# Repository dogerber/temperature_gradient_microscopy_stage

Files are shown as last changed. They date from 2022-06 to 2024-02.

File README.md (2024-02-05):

# Temperature Gradient Microscopy Stage


Microscopy stage with two temperature controlled metal block and a translational frame to move a sample in the temperature gradient by [D. Gerber](https://orcid.org/0000-0002-4231-0694) from the (now retired) [Soft and Living Materials Group at ETH Zürich](https://softliv.mat.ethz.ch/).

Detailed instructions to build the setup can be found in the [wiki](https://github.com/gerberli/temperature_gradient_microscopy_stage/wiki/).

  > [Building your own setup](https://github.com/dogerber/temperature_gradient_microscopy_stage/wiki/Building-your-own-Setup) 

  > [User manual (softliv group)](https://github.com/gerberli/temperature_gradient_microscopy_stage/wiki/Operation-manual)

This has been used for the following publications: 
* [Stress accumulation by confined ice in a temperature gradient (PNAS)](https://www.pnas.org/doi/10.1073/pnas.2200748119)
* [Polycrystalinity enhances stress build-up around ice (PRL)](https://pubmed.ncbi.nlm.nih.gov/38039453/)
* [Dehydration drives damage in the freezing of brittle hydrogels](https://arxiv.org/abs/2401.12871)

# Setup overview
The setup consists of a PID control loop, where an Arduino microcontroller regulates the voltage for two peltier devices. Thermistors are placed in two copper blocks of variable spacing above the peltier devices and the opposite side of the peltier devices is held at room temperature by water cooling. The sample is placed on the copper block and can be moved relative to the temperature gradient by a linear actuator.

**Stage head**

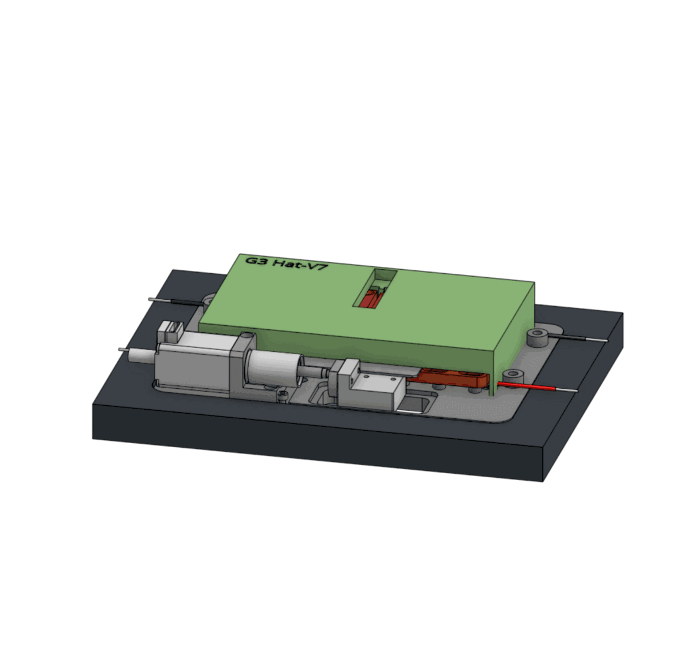
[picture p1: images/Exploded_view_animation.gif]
 
 
 **Controller box**
 
 

**Schematic**

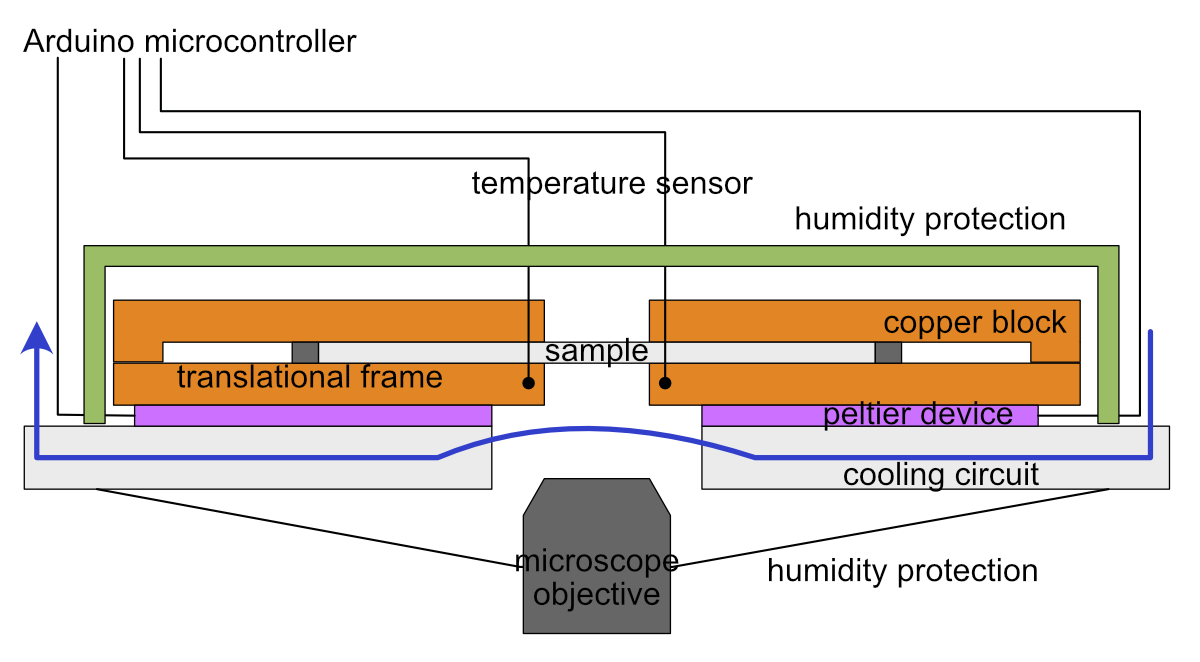
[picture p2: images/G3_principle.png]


# Features
* 0.05 K temperature accuracy, when calibrated
* 0.01 K temperature stability
* Temperature range -25 to 60 °C (colder possible, if using coolant below room temperature)
* Variable spacing between metal blocks of 0-1 cm
* Translation of sample in the temperature gradient with 1.9 cm travel range and 300 nm stepsize
* Optional datalogging to microSD-card
* Optimized for microscope stages with 160x110 mm opening "Universal insert" [I-3091](https://www.asiimaging.com/products/stages-inserts/160-x-110-mm-slide-inserts/), but can be adapted

# Acknowledgement
Lawrence Wilen, Christian Furrer and Robert Style helped with the design of this stage and controller. The menu system used is [GEM](https://github.com/Spirik/GEM) by [Spirik](https://github.com/Spirik).

Inspiration for this stage was also taken from [Prof. Sylvain Devilles group](https://www.sciencedirect.com/science/article/pii/S0304399118300536).

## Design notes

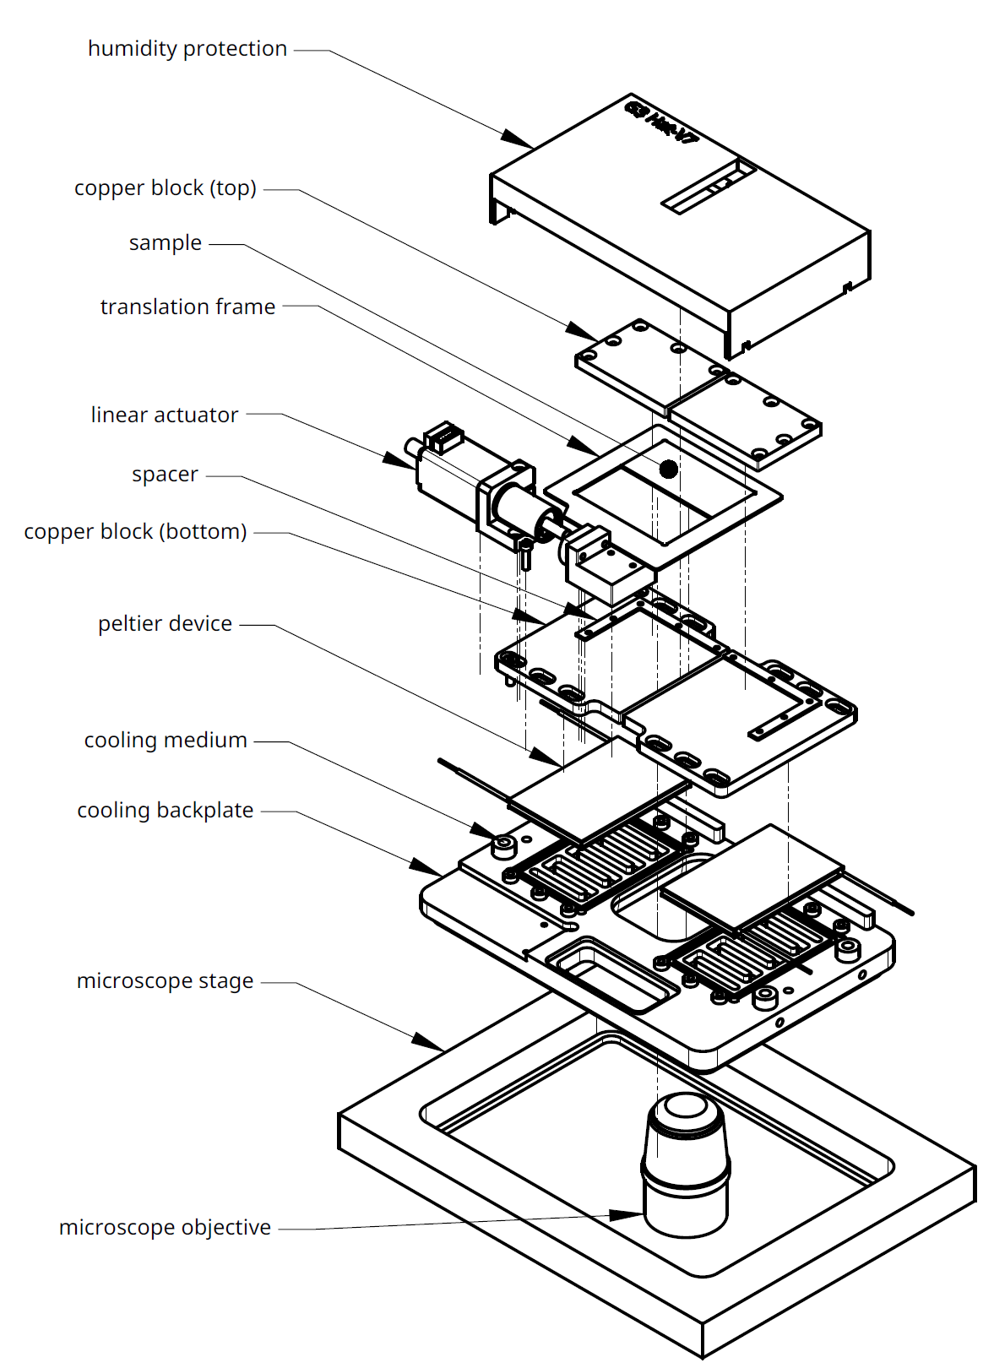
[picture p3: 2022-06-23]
images/stage_head_overview.png

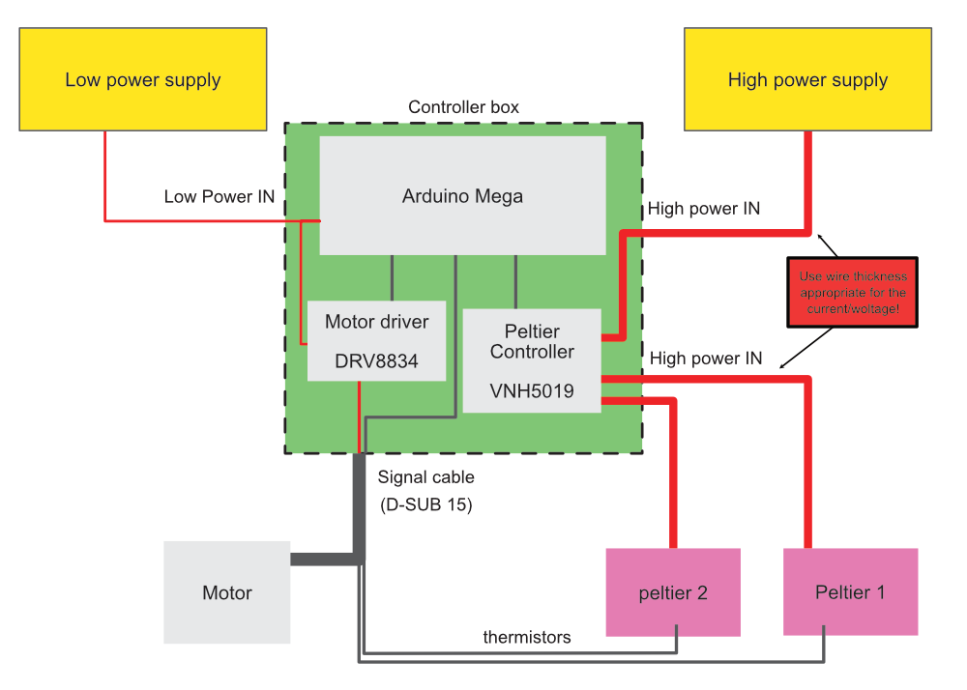
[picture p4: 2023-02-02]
images/power wire schematic.png

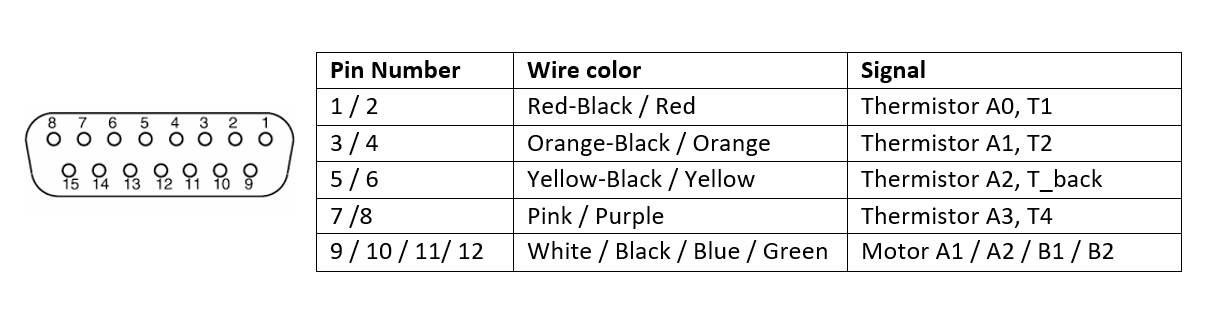
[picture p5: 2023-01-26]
images/dsub-15_pinout.png

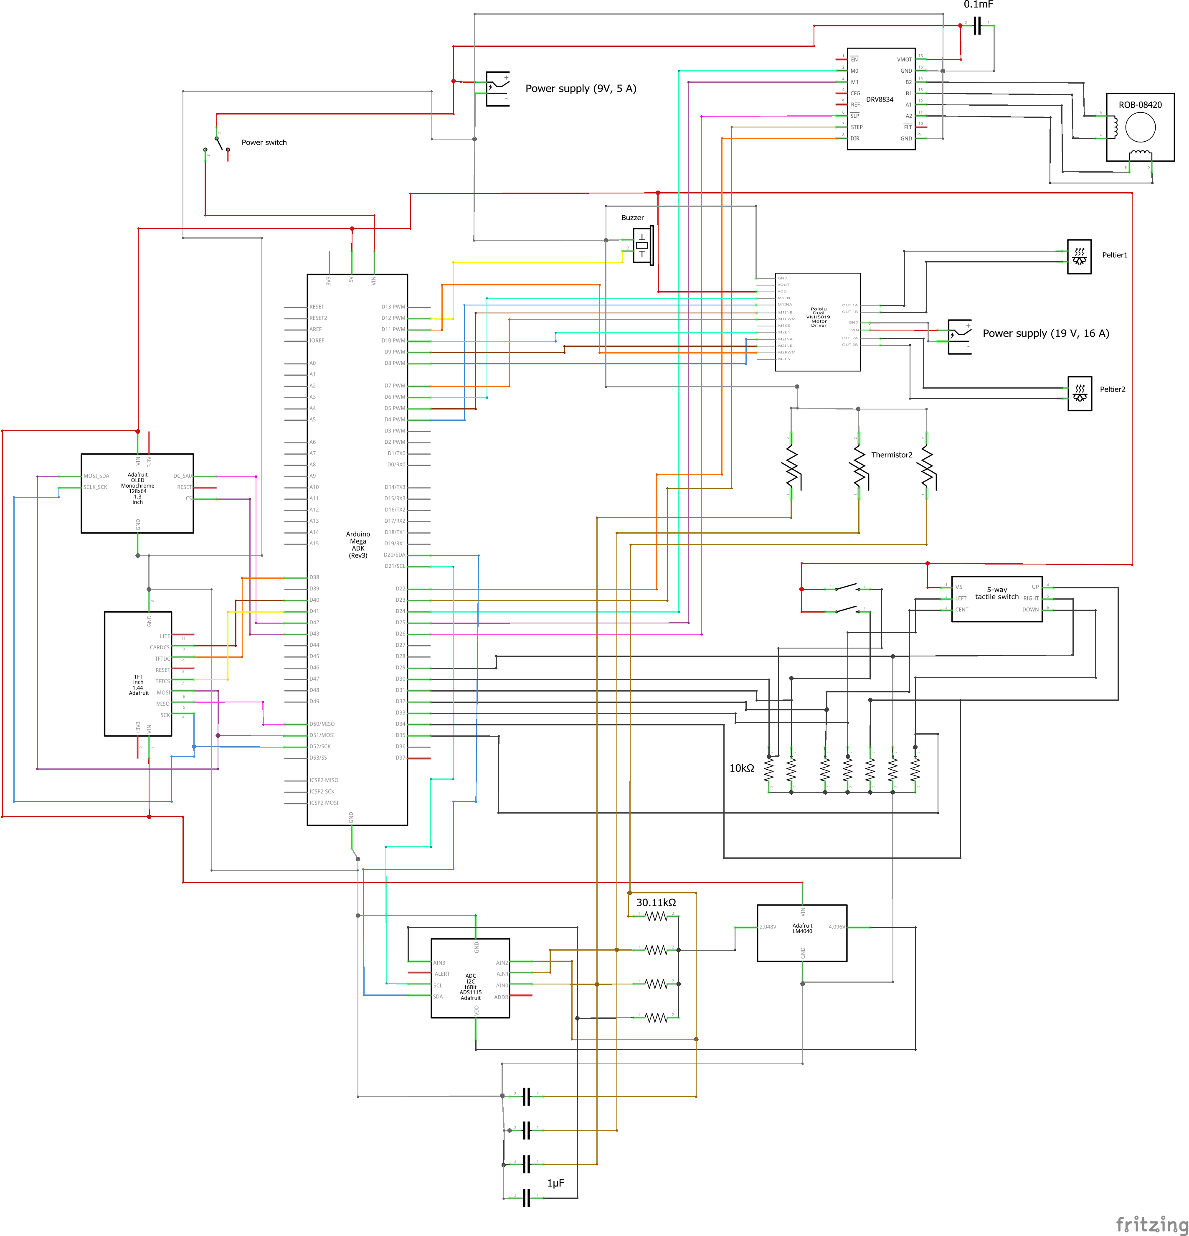
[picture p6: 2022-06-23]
wiring_diagrams/Gelatiera_III_schematic.png

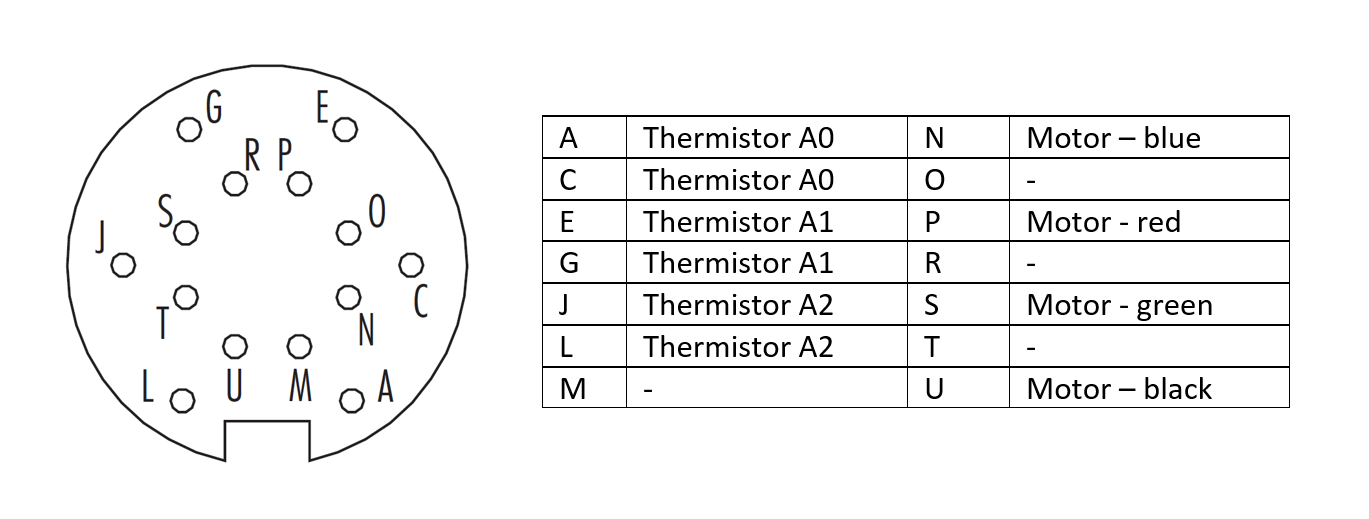
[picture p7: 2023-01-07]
images/signal_cable_layout.png

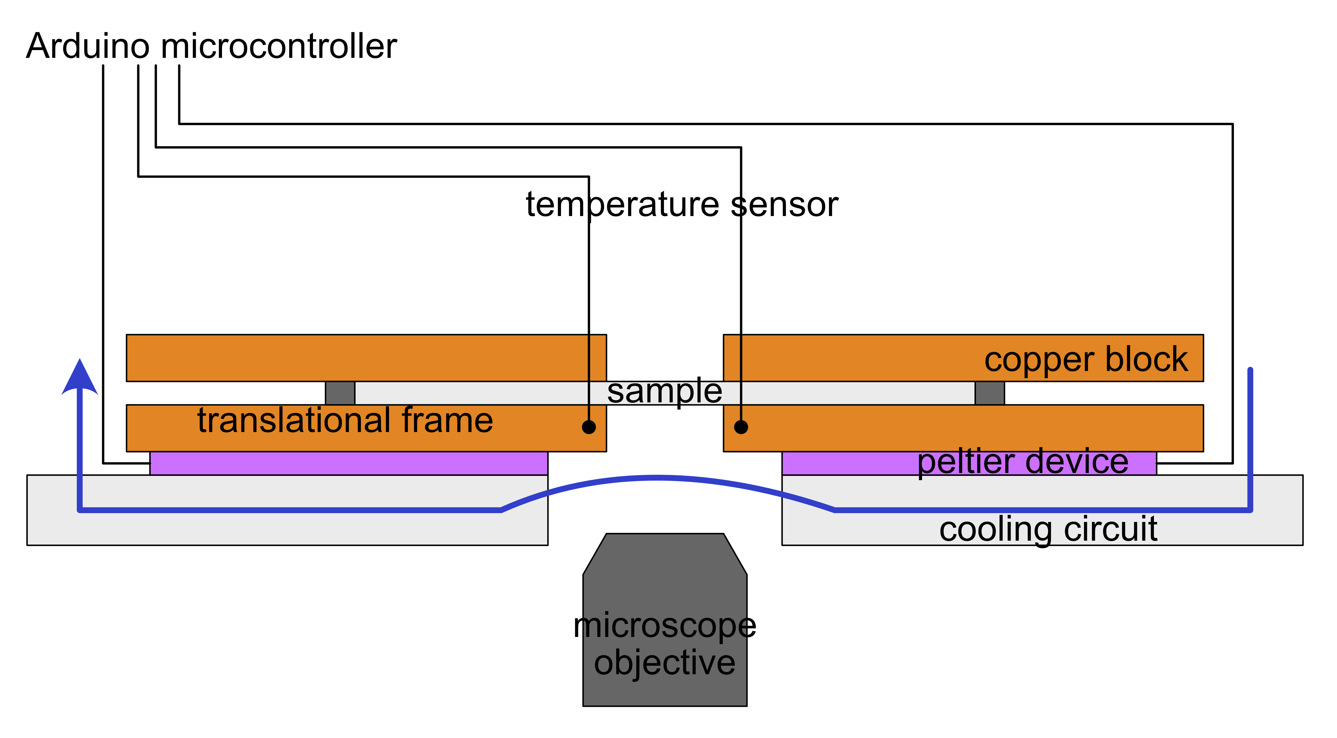
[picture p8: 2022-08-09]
images/G3w_principle.png

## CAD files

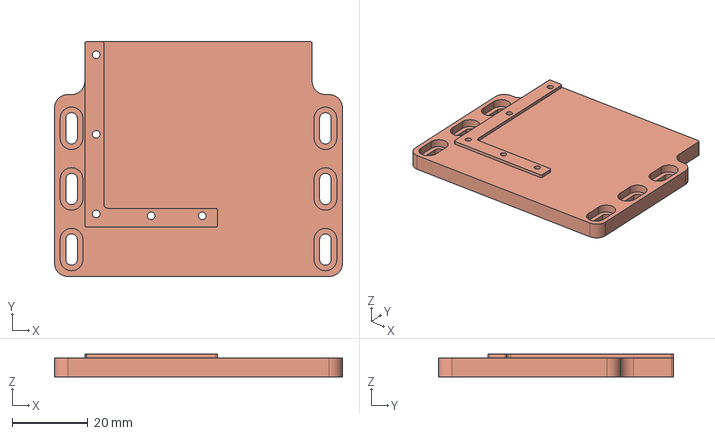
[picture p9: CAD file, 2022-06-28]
CAD_files_stage_head/Copper_block_left_bottom.step
76.0 x 62.0 x 6.00 mm

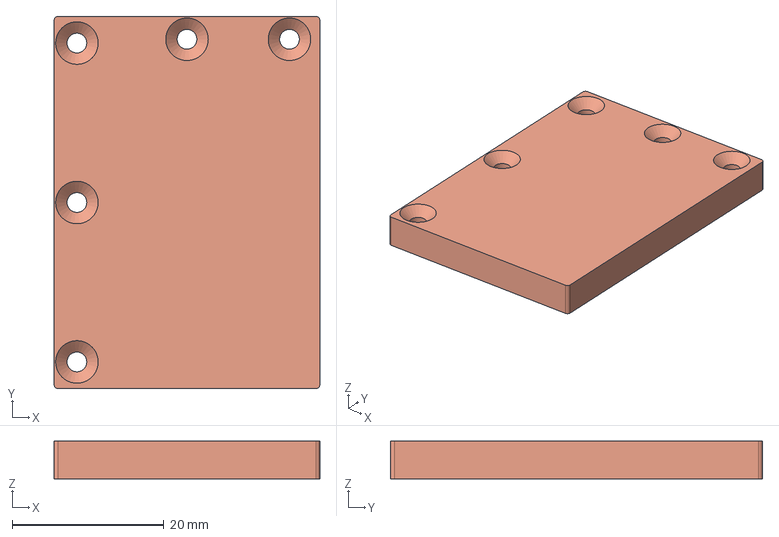
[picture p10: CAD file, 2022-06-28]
CAD_files_stage_head/Copper_block_right_top.step
35.0 x 49.0 x 5.00 mm

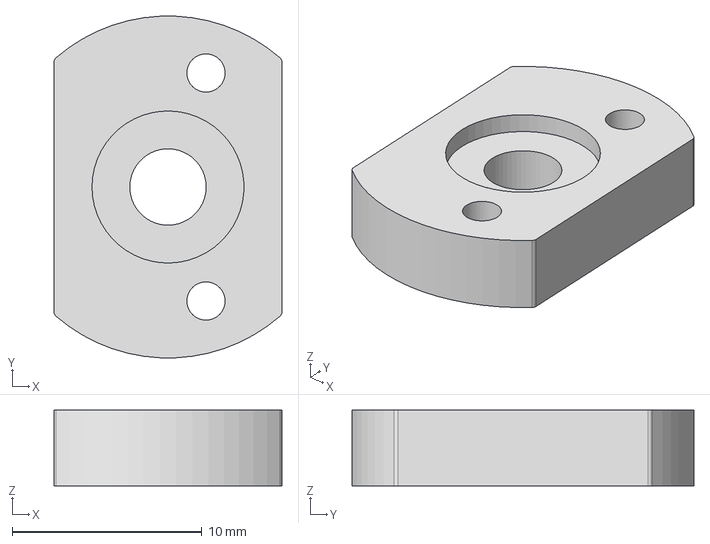
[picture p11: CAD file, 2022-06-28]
CAD_files_stage_head/Motor_connection_to_slider.step
12.0 x 18.0 x 4.00 mm

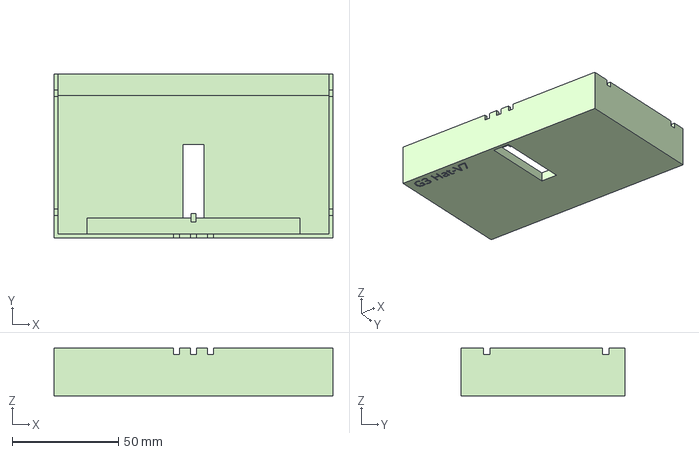
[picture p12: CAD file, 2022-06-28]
CAD_files_stage_head/Enclosure.step
131.0 x 77.0 x 22.5 mm

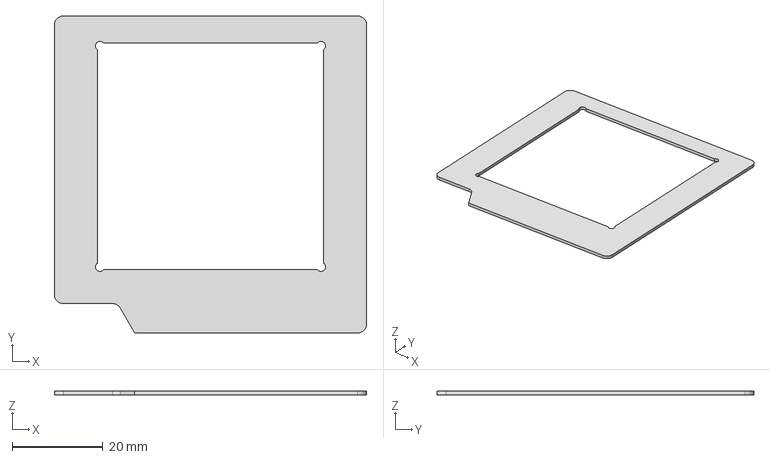
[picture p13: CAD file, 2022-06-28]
CAD_files_stage_head/Motor_translational_frame.step
69.0 x 70.0 x 0.9 mm

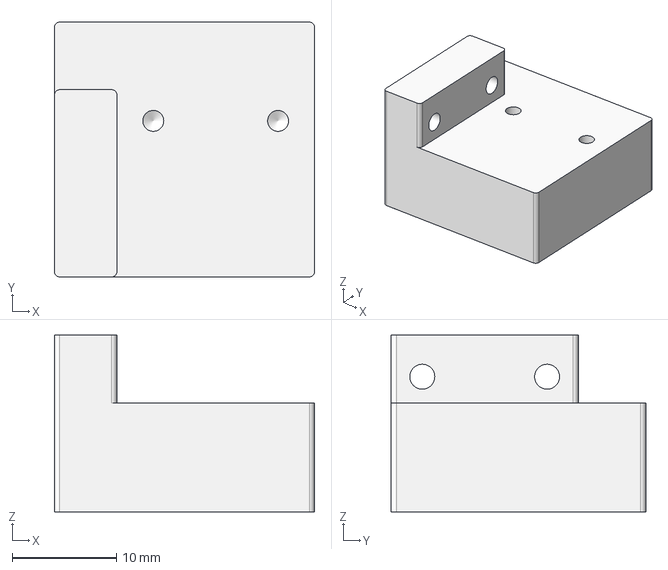
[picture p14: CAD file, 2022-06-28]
CAD_files_stage_head/Motor_slider.step
25.0 x 24.5 x 17.0 mm

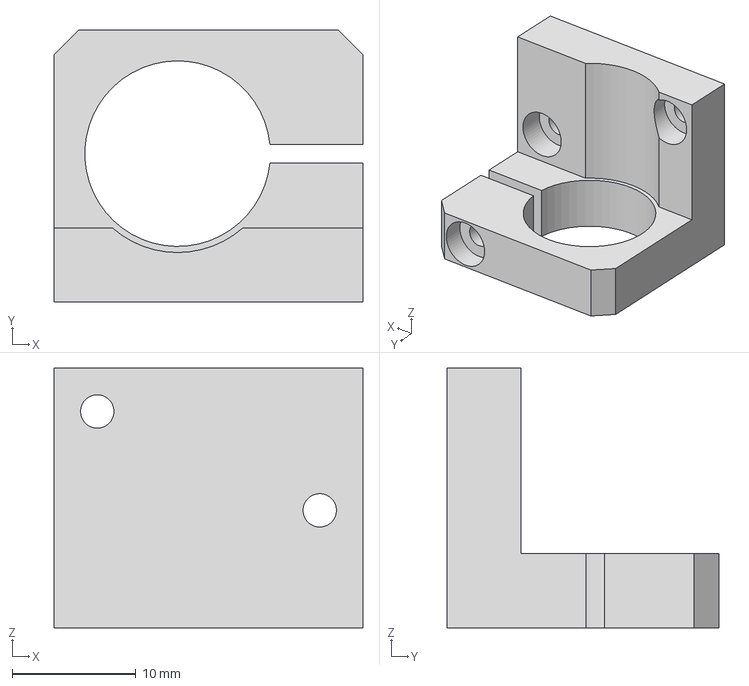
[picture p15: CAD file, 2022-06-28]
CAD_files_stage_head/Motor_mount_to_backplate.step
25.0 x 22.0 x 21.0 mm

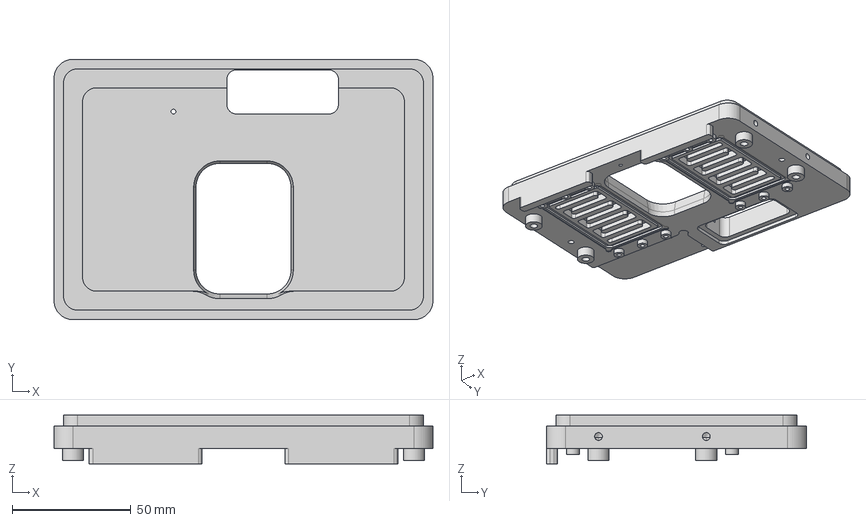
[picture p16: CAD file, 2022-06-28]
CAD_files_stage_head/Cooling_backplate.step
159.7 x 109.7 x 20.5 mm

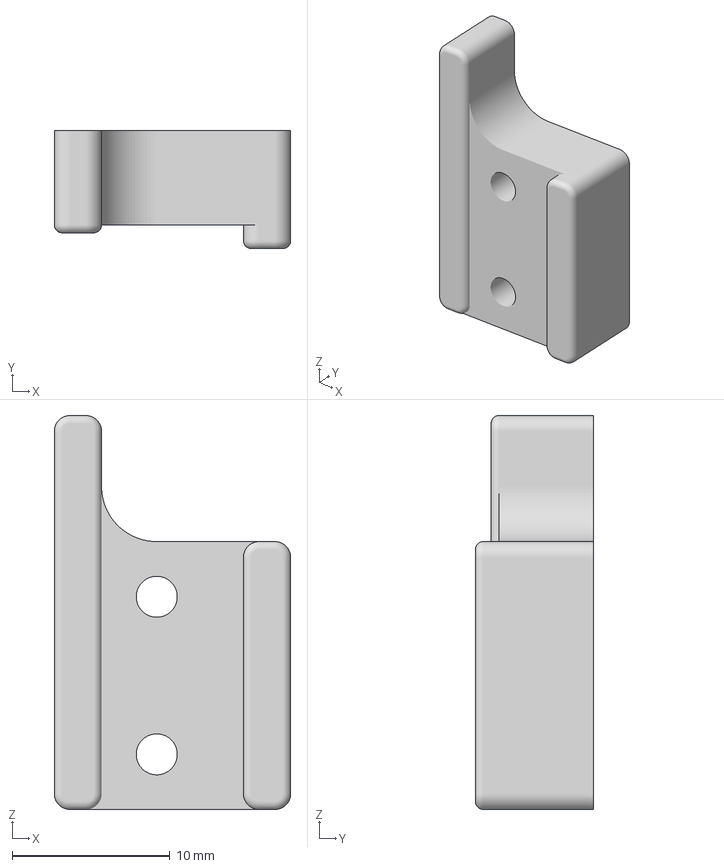
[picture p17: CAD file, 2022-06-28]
CAD_files_stage_head/Motor_slider_to_frame_connection.step
15.0 x 7.50 x 25.0 mm

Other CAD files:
CAD_files_stage_head/Copper_block_right_bottom.step
CAD_files_stage_head/Copper_block_left_top.step

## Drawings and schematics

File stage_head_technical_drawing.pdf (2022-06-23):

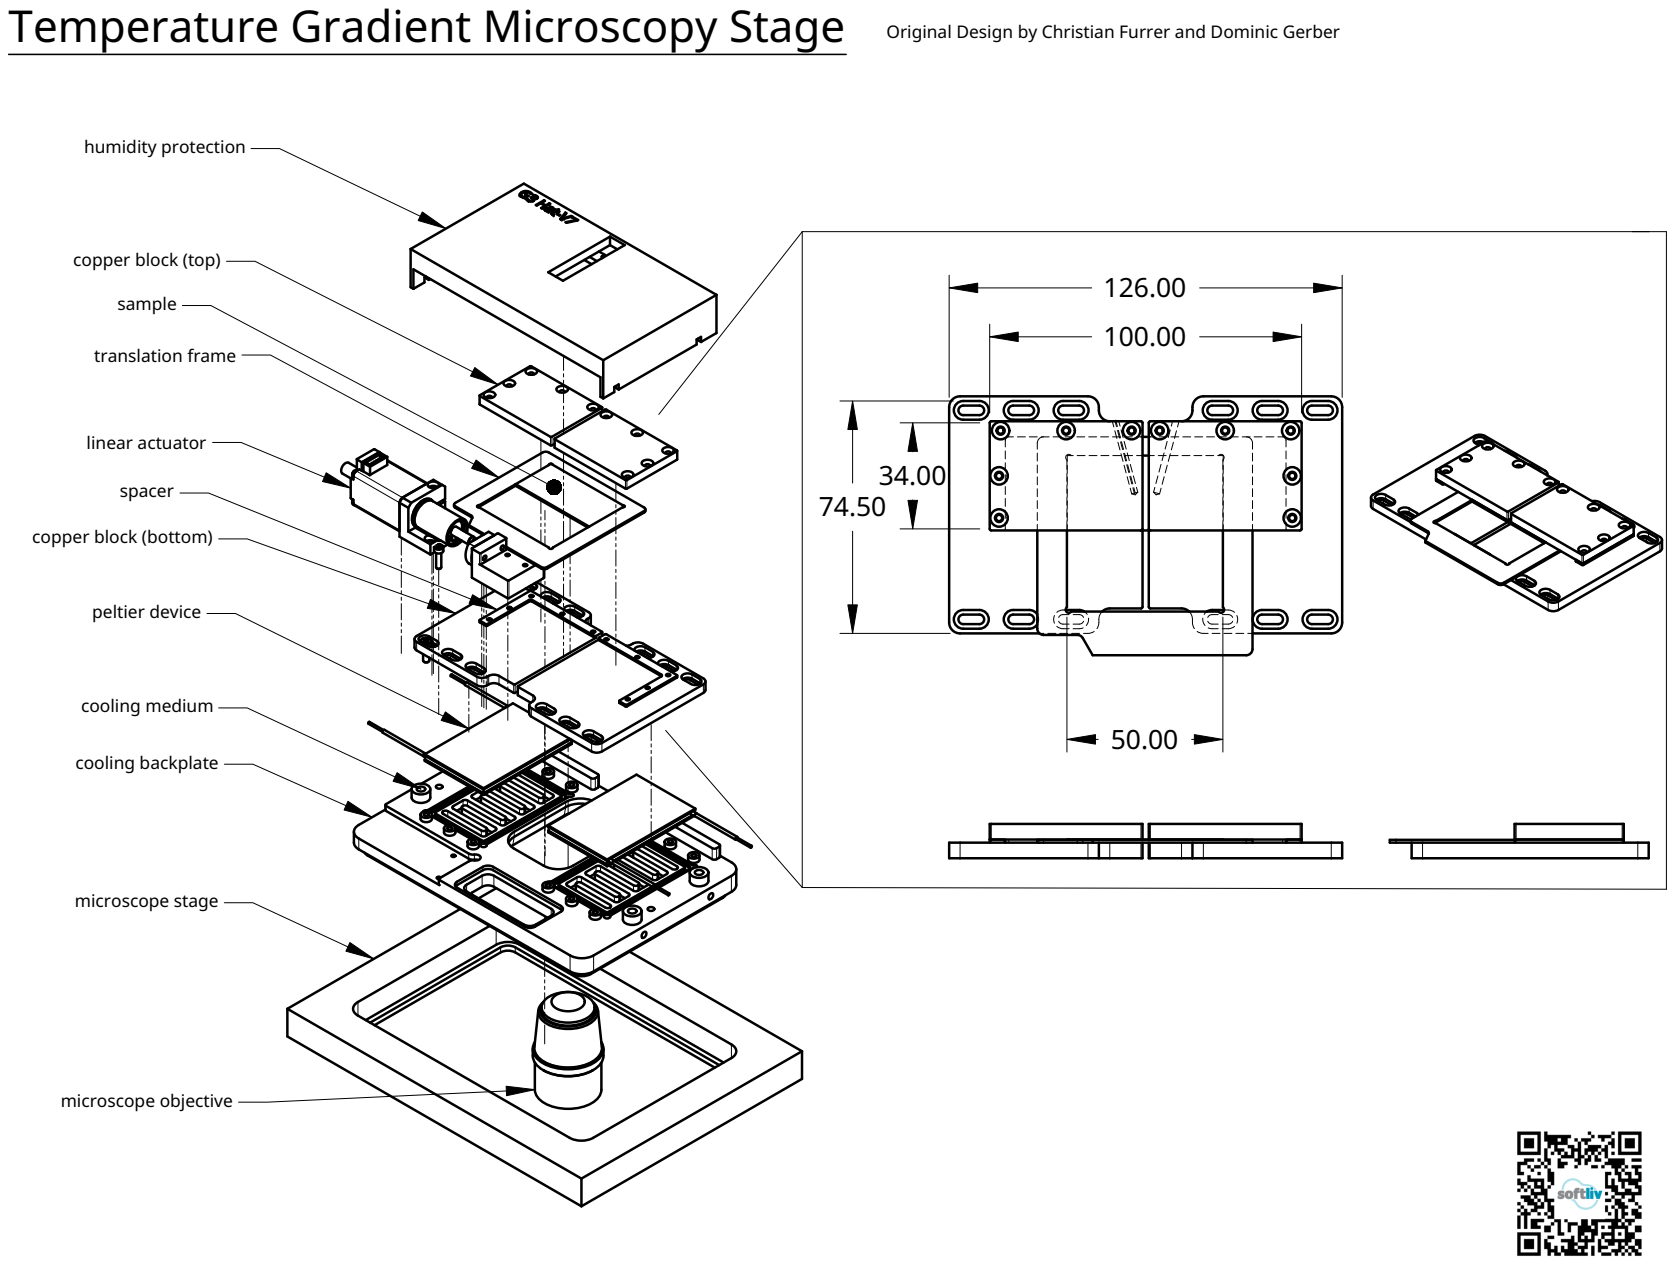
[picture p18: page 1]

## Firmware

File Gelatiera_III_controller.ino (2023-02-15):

// Gelatiera III Controller
//
// For Temperature Gradient stage with two Peltier Elements and a linear actuator
// to be controlled by an Arduino Mega
// Original Code by Dominic Gerber and Lawrence Wilen
//
// ----- Changelog: ------
// v1.0.5
//    - added screensaver to prevent pixel burn
// v1.0.4
//    - added logging of peltier power, if enabled
// v1.0.3:
//    - T3 sensor calibration 221109
// v1.0.2:
//    - Changed calibration for T3 temperature sensor
//    - added welcome message
//    - removed Adafruit_ImageReader, was not used
//    - fixed bug which prevented quick_move_to_0 to work
//    - added safety shutoff if T1/T2 reading is out of range
// More Information at https://github.com/dogerber/temperature_gradient_microscopy_stage
// ------------------------------------------------------------------------------------
#define CODE_VERSION "1.0.5"

//////////////////////////////// Libraries ///////////////////////////////////////////
#include <Adafruit_GFX.h>           // Core graphics library
#include <Adafruit_SSD1351.h>       // (large) Display (https://www.adafruit.com/product/2088), 128x128 pixel
#include <Adafruit_SSD1306.h>       // (small) OLED 1.3 " display (https://www.adafruit.com/product/938), 128x64 pixel
#include <SdFat.h>                  // SD card & FAT filesystem library
#include <Adafruit_SPIFlash.h>      // SPI / QSPI flash library
//#include <Adafruit_ImageReader.h>   // Image-reading functions
#include <GEM_adafruit_gfx.h>       // GEM (https://github.com/Spirik/GEM)
#include <KeyDetector.h>            // GEM 
#include <Adafruit_ADS1X15.h>       // used to measure temperature with ADS1115
#include "DRV8834.h"                // DRV8834 driver for linear actuator


//////////////////////////////// PINS ////////////////////////////////////////////////
// TFT display (large), OLED (small) display and SD card
#define SD_CS    40 // SD card select pin
#define TFT_CS   41 // large  SSD1351 OLED
#define OLED_CS  43 // small SSD1306 OLED
#define TFT_DC   38 // TFT display/command pin, could be combined
#define OLED_DC   42 // TFT display/command pin

// Pololu DRV8834 motor driver for the linear actuator
#define MOTOR_STEPS 200 // Motor steps per revolution. Most steppers are 200 steps or 1.8 degrees/step
#define RPM 120
#define DIR 22
#define STEP 23
#define M0 24
#define M1 25
#define SLEEP 26

// Pololu VNH5019 peltier dual motor driver Pins
#define M1A 4
#define M1B 5
#define M1ENABLE 6
#define M1PWM 7
#define M2A 8
#define M2B 9
#define M2ENABLE 10
#define M2PWM 11

// shared pins (SPI BUS)
#define TFT_RST  -1 // set to -1 and connect to Arduino RESET pin
#define OLED2_RST -1

// Various
#define BUZZER_PIN 12 // for the buzzer

// Navigating Buttons for GEM
const byte downPin = 35;
const byte leftPin = 32;
const byte rightPin = 37;
const byte upPin = 34;
const byte cancelPin = 31;
const byte okPin = 30;

/* Summary of PINS used
   4 VNH5019 - M1A
   5 VNH5019 - M1B
   6 VNH5019 - M1ENABLE
   7 VNH5019 - M1PWM
   8 VNH5019 - M2A
   9 VNH5019 - M2B
   10 VNH5019 - M2ENABLE
   11 VNH5019 - M2PWM
   12 BUZZER-PIN

   22 DRV8834 - DIR
   23 DRV8834 - STEP
   24 DRV8834 - M0
   25 DRV8834 - M1
   26 DRV8834 - Sleep

   30 Button - OK
   31 Button - cancel
   32 Joystick - Left
   36 Joystick - Push ? (not used)
   34 Joystick - Up
   35 Joystick - Down
   37 Joystick - Right

   38 TFT_DC
   40 SD_CS "CCS" on display
   41 TFT_CS
   42 OLED_DC
   43 OLED_CS

   50 MISO
   51 MOSI
   52 SCK, Clock

   SCL, SDA (I2C): for ADS1115 (temperature measurement)
*/



//////////////////////////////// Global Variables //////////////////////////////////////


// Settings
#define T_MAX 45 // in Celsius, maximum allowed temperature, should be at least 5 degrees out of operation range
#define T_MIN -40 // peltier will shut down when this is reached to avoid damage
#define T_RANGE_MAX 40 // this will be the maximum possible set temperature
#define T_RANGE_MIN -35
#define MAX_COOLING_PLATE_TEMPERATURE 40 // will shut all cooling down when reached until user enables it again
const boolean do_Serial_communication = true; // good for debugging, but makes code slower
boolean do_beep = true;

// Warning / Alarms
unsigned long t_last_alarm_beep;
#define ALARM_BEEP_INTERVAL_MS 10000
String warning_string = "";
unsigned long t_last_warning_message = 0;
#define WARNING_MESSAGE_DISPLAY_TIME 30000 // [ms]

// Temperature control
float SetTemp1 = 25.0;
float PlanTemp1 =  25.0; // PlanTemp is the target, SetTemp the current setting (when changing slowly)
float SetTemp2 = 25.0;
float PlanTemp2 = 25.0;

boolean commitChangesT = false; //
unsigned long t_commitChangesT_last_step = 0;
float TempChangeRate = 00.00; // [K/min] how fast temperature is changed, 0 for instant change

// Temperature measurement (ADS1115)
float Temp0; // Actual Temperature measured
float Temp1;
float Temp2;
float Temp3;
float T_Peltier_1;
float T_Peltier_2;
float T_cooling_plate;
float T_sensor;
boolean displayT3 = false; // show T_sensor on OLED display

const float R_Ref0 = 30.13; // Known resistances of the voltage divider
const float R_Ref1 = 30.11; // measured with old Multimeter before assembly
const float R_Ref2 = 30.13;
const float R_Ref3 = 30.11;
const float Volt_in = 2.048; // [V] depending on wiring of LM4040
const float T_num_average = 10.0; // number of readings of the thermistor resistance. More = slower but less noisy
float R0; // Resistance of the thermistor to be measured
float R1;
float R2;
float R3;


// Motor control
long mot_position; // current position [steps]
long mot_SetPosition; // current target position [steps]
long mot_PlanPosition; // ultimate position to be reached [steps]
float mot_PlanPosition_um; // ultimate position to be reached [um], in GEM
long mot_maxPos = 25000; // [steps] max distance in steps from the middle (=0) in both directions
// linear actuator travels 1 mm per rotation, has 200 normal steps, here with 32 microsteps, so 1mm = 32*200 microsteps
float mot_speed = 100.00; // [micrometers/minutes]
long mot_stepsToDo; // [steps] for current movement step
float mot_stepsize = 0.315305;// in [mum/step]
boolean commitMovement = false; // starts movement of actuator
long last_mot_position_saved; // keep track of value written to SD card to only write when it changed
boolean mot_position_loaded = false; // initialize as NaN so it's read from SD card
boolean mot_holding = true; // stepper.enable() -> causes motor to be held and unmovable
boolean mot_first_movement = true;
char filename_mot[GEM_STR_LEN] = "motpoy.txt";
unsigned long mot_t_startMovement;
long mot_Position_startMovement;
const float speedConversionFactor = 1 / (mot_stepsize * 60 * 1000); // mot_speed is given in mum/min, we need it in [steps/millis]
float mot_QuickMoveStep_um = 200; // [um]

// Variables for PID of peltier control (VNH5019)
boolean enablePeltiers = true;
float errorval1; // this stores the difference between the setpoint and the actual temperature
float errorval2;
float previous_errorval1 = 0;
float previous_errorval2 = 0;
float peltier1; // this stores the actual power level you are sending to the peltier device; can be negative or positive
float peltier2;
float peltier1_percentage; // for displaying power usage
float peltier2_percentage;
float Pgain = 305; // the proportional gain
float Igain = 1.9; // the integral gain
float Dgain = 4000; // differential gain
const float antiwindval = 2; // a value that keeps the integrator from integrating up if you are far from your setpoint
float offset1 = 0; // stores the value in the integrator
float offset2 = 0;
float offset_dif1 = 0;
float offset_dif2 = 0;
unsigned long peltier_t_last_tp;

// Screens
#define SCREEN_WIDTH  128 // Screen dimensions in pixel
#define SCREEN_HEIGHT 128
#define SCREEN2_WIDTH  128
#define SCREEN2_HEIGHT 64
unsigned long t_lastButtonPress = 0;
unsigned long t_untillScreenOff = 300000; // [ms] large screen tft is turned off after this time to save pixels from burning out
boolean screenSaver_boolean = false; // [boolean] keeps track of if the screensaver is currently on or not

// Menu and data logging
boolean do_plot_temperatures = false; // enables Serial print of T values to be plotted in Arduino IDE
unsigned long t_MenuLastRefresh = 0;
int runtime = 0;  // this is wrong, should be unsigned long, but that conflicts with GEM-menu item
int time_for_one_loop_ms = 0;
boolean enableDataLogging = false;
char filename_log[GEM_STR_LEN] = "log01.txt";  // not to long please, max 8 char i think



/////////////////////////////////Setup GEM Menu and SD-card//////////////////////////////////////
// SD card
SdFat                SD;         // SD card filesystem
SdFile myFile;
//Adafruit_ImageReader reader(SD); // Image-reader object, pass in SD filesys

// Screens
Adafruit_SSD1351 tft = Adafruit_SSD1351(SCREEN_WIDTH, SCREEN_HEIGHT, &SPI, TFT_CS, TFT_DC, TFT_RST); // large screen
Adafruit_SSD1306 oled2 = Adafruit_SSD1306(SCREEN2_WIDTH, SCREEN2_HEIGHT, &SPI, OLED_DC, OLED2_RST, OLED_CS); // small screen

// Temperature measurement
Adafruit_ADS1115 ads;  // load library to run ADS1115, used for temperature measurement

// Motor driver DRV8834 for linear actuator
DRV8834 stepper(MOTOR_STEPS, DIR, STEP, SLEEP, M0, M1);


// GEM (Menu system)
// Array of Key objects that will link GEM key identifiers with dedicated pins
Key keys[] = {{GEM_KEY_UP, upPin}, {GEM_KEY_RIGHT, rightPin}, {GEM_KEY_DOWN, downPin}, {GEM_KEY_LEFT, leftPin}, {GEM_KEY_CANCEL, cancelPin}, {GEM_KEY_OK, okPin}};
KeyDetector myKeyDetector(keys, sizeof(keys) / sizeof(Key)); // Create KeyDetector object

// Main page
GEMItem menuItemEnablePeltiers("T control:", enablePeltiers);
void checkPlanTemps(); // forward declaration?
GEMItem menuItemSetTemp1("Set T1:", PlanTemp1, checkPlanTemps);
GEMItem menuItemSetTemp2("Set T2:", PlanTemp2, checkPlanTemps);
GEMItem menuItemTemp3("T3:", T_sensor, false); // for gradient measurement in the experimental cell
GEMItem menuItemChangeRate("[K/min]:", TempChangeRate);
void doCommitChangesT(); // forward declaration?
GEMItem menuItemCommit("Change T:", commitChangesT, doCommitChangesT);

// Motor control
GEMItem menuItemTitleActuator("--Actuator ", "      --", false);
void doCheckPlanPosition();
GEMItem menuItemMotPlanPosition("Target:", mot_PlanPosition_um, doCheckPlanPosition);
GEMItem menuItemMotSpeed("[um/min]:", mot_speed);
void doCommitMovement(); // forward declaration
GEMItem menuItemCommitMovement("Move:", commitMovement, doCommitMovement);
void resetMotPosition(); // forward declaration
GEMItem menuItemResetMotPosition("Calibrate 0", resetMotPosition);
GEMItem menuItemMotHold("Motor hold:", mot_holding, commitMovement);  // last option locks the option when movement is in progress

GEMItem menuSDFilename("Filename", filename_log);
GEMItem menuEnableDataLogging("Log data", enableDataLogging);

GEMItem menuCodeVersion("Code v.", CODE_VERSION, true);
GEMItem menuRuntime("Time [s]:", runtime, true);

GEMPage menuPageMain("Gelatiera III");
GEMItem menuItemMainLink("Main Menu", menuPageMain);
GEMItem menuItemMainLink2("Main Menu", menuPageMain);
GEMItem menuItemMainLink3("Main Menu", menuPageMain);
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
